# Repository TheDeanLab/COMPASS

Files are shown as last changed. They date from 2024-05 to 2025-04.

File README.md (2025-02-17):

<h1 align="center">
COMPASS

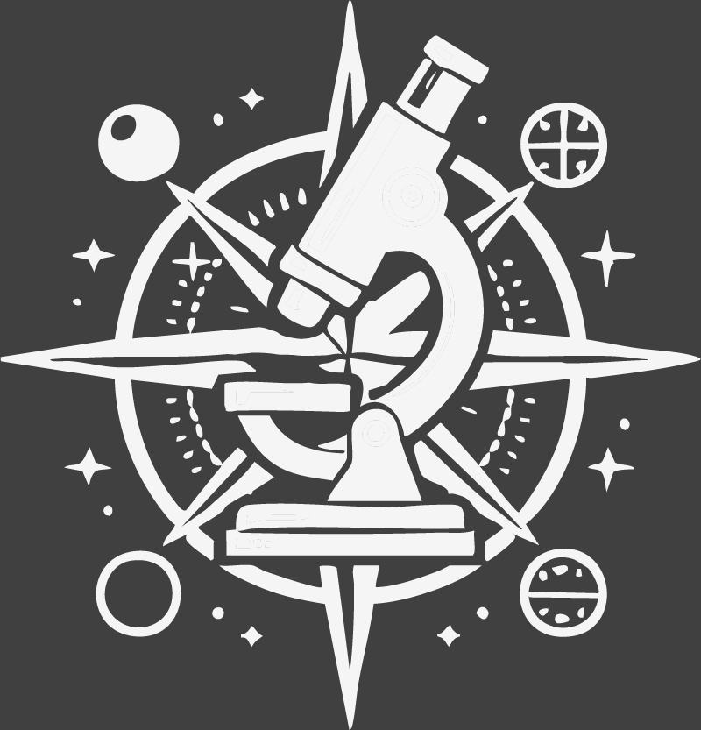
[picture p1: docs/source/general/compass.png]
COMPASS


<h3 align="center">
	Cost-Effective, Open-Source, Light-Sheet Microscopy Solutions for for Sub-Cellular Imaging.
</h3>
</h1>

**COMPASS** aims to democratize high-resolution light-sheet fluorescence microscopy. By combining **modular optomechanics**, **cutting-edge lens simulations**, and **intelligent software**, **COMPASS** enables the rapid assembly of light-sheet fluorescence microscopes that deliver ~235 nm lateral and ~465 nm axial resolution in a user-friendly package.

## Motivation

Cellular behavior is orchestrated by diverse signaling mechanisms that often hinge on **molecular events precisely organized in space and time**. These events include rapid, localized protein interactions that drive processes such as cell division, migration, and differentiation. **COMPASS** addresses the need for **high-resolution live-cell imaging**, empowering researchers to:

- Visualize spatially regulated processes.
- Collect quantitative 3D time-lapse data.
- Bridge molecular probe design and advanced computational image analysis.

## Goal

The overarching goal is to provide a **modular, cost-effective 3D light-sheet microscope** that:
- Can be assembled with minimal prior optics expertise.
- Consistently achieves ~235 nm lateral and ~465 nm axial resolution.
- Seamlessly integrates with our user-friendly, **intelligent imaging software** [navigate](https://github.com/TheDeanLab/navigate).
- Streamlines data acquisition, drastically reducing barriers to cutting-edge microscopy.

## Key Features

1. **High-Resolution Optics**  
   - Optical designs extensively **simulated in Ansys Zemax OpticStudio** to ensure robust performance across the visible spectrum.
   - Thorough **tolerance analysis** to maintain alignment and resolution in non-specialist environments.

2. **Rugged Mechanical Design**  
   - **Computer aided design (CAD) with Autodesk Inventor** for stress testing and mechanical reliability.
   - **Xometry** manufacturing ensures precision component fabrication.
   - **Dowel pins** and **Thorlabs Polaris mounts** allow reproducible alignment of optical elements.

3. **Easy-to-Source Components**  
   - Optics primarily sourced from **Thorlabs**, with **Polaris mounts** for stable positioning.
   - Motion control solutions (X, Y, Z, Focus, Sample Scanning) from **Applied Scientific Instrumentation**.
   - Open-hardware ethos with minimal custom parts to reduce cost and wait times.
   - Detailed step-by-step assembly instructions,

4. **Intuitive Control Software**  
   - Built to interface seamlessly with [navigate](https://github.com/TheDeanLab/navigate).
   - Automated routines for calibration, 3D volume acquisition, and intelligent imaging.

## Getting Started

- **Review the [Documentation](https://thedeanlab.github.io/COMPASS/)**
- **Procure Hardware**
- **Download and Install** [navigate](https://github.com/TheDeanLab/navigate)
- **Assemble Hardware**
- **Optimize Alignment**
- **Validate Performance**

## Authors

- John Haug, Ph.D.
- Kevin M. Dean, Ph.D.

## Funding

- **UTSW-UNC Center for Cell Signaling Analysis**  NIH NIGMS RM1GM145399
- **Center for Metastatic Tumor Imaging**  NIH NCI U54CA268072

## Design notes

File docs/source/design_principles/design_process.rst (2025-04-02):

.. _design-home:

##############
Design Process
##############

---------------

Initial Lens Selection
______________________

Prior to starting optical simulations in Zemax, it's convenient to start with straightforward
calculations to determine which lenses to use in the optical train to achieve the desired field of view (FoV) for your
detection path. In our case, our detection path consisted of a 400 mm tube lens and a Nikon 25x/1.1 numerical aperture (NA) immersion detection objective.

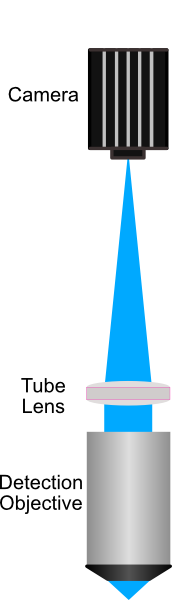
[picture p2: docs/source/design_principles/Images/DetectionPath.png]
Schematic of a standard, widefield detection path.


   **Figure 1:** A simple schematic for a widefield detection path. Here, a detection objective captures light, which is then focused onto the active sensor of a CMOS camera using a tube lens.

.. sidebar:: **Calculating the Focal Length of an Objective**
   :class: sidebar-note

   The focal length (:math:`f`) of a microscope objective can be determined using the **nominal focal length** of
   the manufacturer's standard tube lens and the **objective’s magnification**:

   .. math::

      f = \frac{f_{\text{tube lens}}}{M}

   where:

   - :math:`f_{\text{tube lens}}` is the standard focal length of the tube lens.
   - :math:`M` is the nominal magnification of the objective.

   Standard tube lens focal lengths vary by manufacturer:

   - **Nikon / Zeiss**: 200 mm
   - **Olympus**: 180 mm

   **Example Calculation**
   For a **Nikon 25× NA 1.1 objective**, the focal length is calculated as:

   .. math::

      f = \frac{200 \text{ mm}}{25} = 8 \text{ mm}

To determine the target FoV, start with determining the final magnification (M) of the system using the ratio of the focal lengths of the tube lens (*f*:subscript:`TL`) and the detection objective (*f*:subscript:`DO`, Equation 1.).

.. math::

   M = \frac{f_{\text{TL}}}{f_{\text{DO}}}

From there, determine the resulting FoV of the detection path by dividing the total camera sensor size (in mm) by the magnification, and then converting into microns (Equation 2).

.. math::

   \text{FoV} \ (\mu m) = \left( \frac{W_{\text{Sensor}}}{M} \right) \times 1000

For our system, where *f*:subscript:`TL` = 400 mm, *f*:subscript:`DO` = 8 mm, and W :subscript:`Sensor` = 13 mm,
this resulted in a FoV of ~266 :math:`\mu m`, meaning that we want to select lenses in our illumination path
to produce a light sheet as close to 266 :math:`\mu m` in length as we can achieve.

The overarching goal of a standard optical system is to both mold light into a particular shape and direct it to a
particular location. In our case, our optical system works to convert an input gaussian beam into a thin light sheet that illuminates our sample. There are a few sets of criteria that help guide our potential lens selection:

    * As mentioned, we want our final light sheet size to ideally cover the full FoV of our detection path (~266 μm)
    * At the focus of our cylindrical lens, we want the beam spot size to stay under the size of our resonant galvo (12 mm diameter)
    * We need the focal distance between the cylindrical lens and the galvo mirror system to be greater than ~55 mm due to mechanical considerations of the mirror mount used

With these criteria in mind, we can calculate a theoretical estimate of what our beam size is after each of our lenses. We
do this by considering every pair of lenses (i.e. Lens 1 & 2, Lens 2 & 3, ...) as a sort of 4F magnification system,
where the resulting image size of the pairs is determined by the ratio of their focal lengths (*f*:subscript:`n`) as follows:

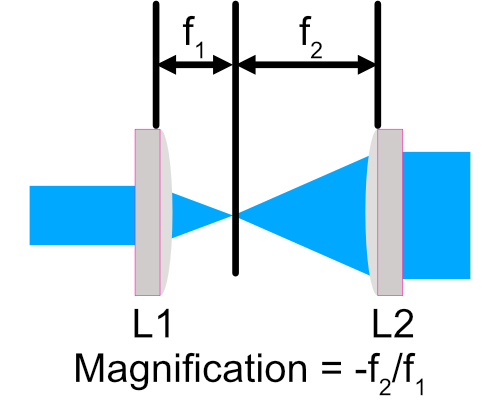
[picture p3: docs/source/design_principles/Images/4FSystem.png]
A diagram of a 4f optical system.


   **Figure 2:** A diagram of a 4f optical system. Here, the ratio of the focal lengths of the lenses determines the magnification of the system.

Essentially, we can cascade these calculations through our lenses and make sure that our choices in their focal
lengths produce our desired beam characteristics as light propagates through the system. In our case,
our chosen system featured 4 lenses from Thorlabs:
`L1 = 30 mm <https://www.thorlabs.com/thorproduct.cfm?partnumber=AC254-030-A>`_,
`L2 = 80 mm <https://www.thorlabs.com/thorproduct.cfm?partnumber=AC254-080-A>`_,
`L3 (Cylindrical) = 75 mm <https://www.thorlabs.com/thorproduct.cfm?partnumber=ACY254-075-A>`_, and
`L4 = 250 mm <https://www.thorlabs.com/thorproduct.cfm?partnumber=AC254-250-A>`_.

We can then take these lens choices and load them into Zemax OpticStudio to verify the characteristics of our system.

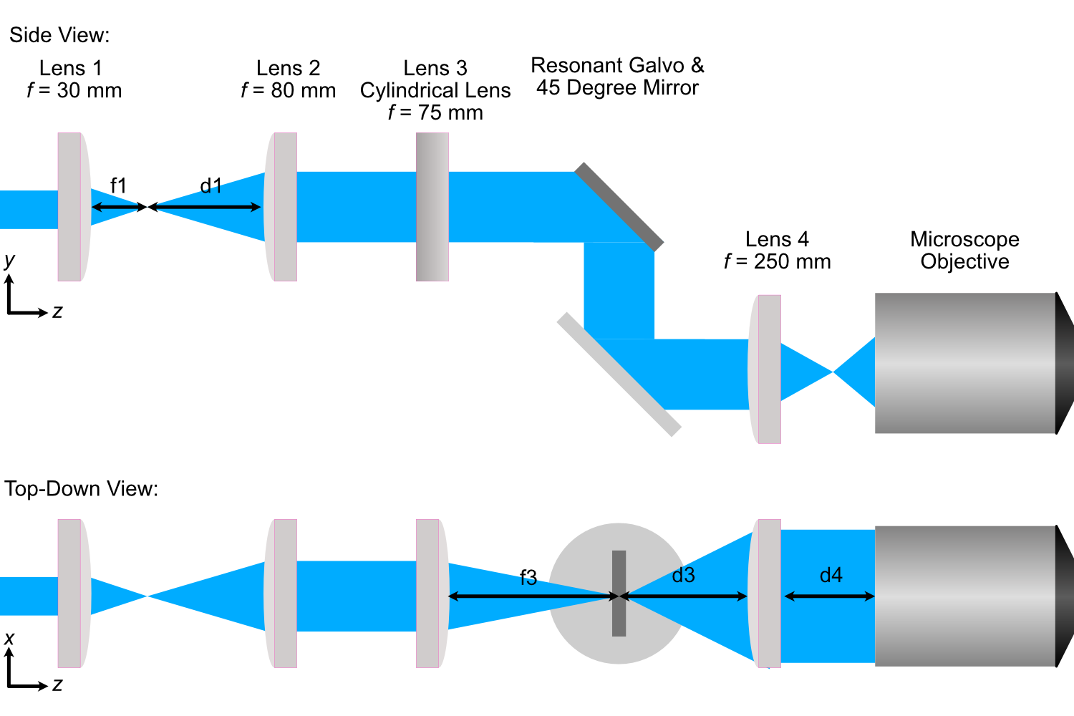
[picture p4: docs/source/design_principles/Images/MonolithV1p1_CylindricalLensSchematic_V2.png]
Top and bottom views of an optical path.


    **Figure 3:** A schematic of the optical path for a light-sheet microscope. The system consists of four lenses, a cylindrical lens, a resonant galvo, a 45-degree mirror, and an illumination objective. Top and bottom views are shown.

----------------

Zemax Simulation Setup Process
______________________________

With our chosen lenses in mind, we can download Zemax files associated with each lens directly from Thorlabs website
and set up our simulation.

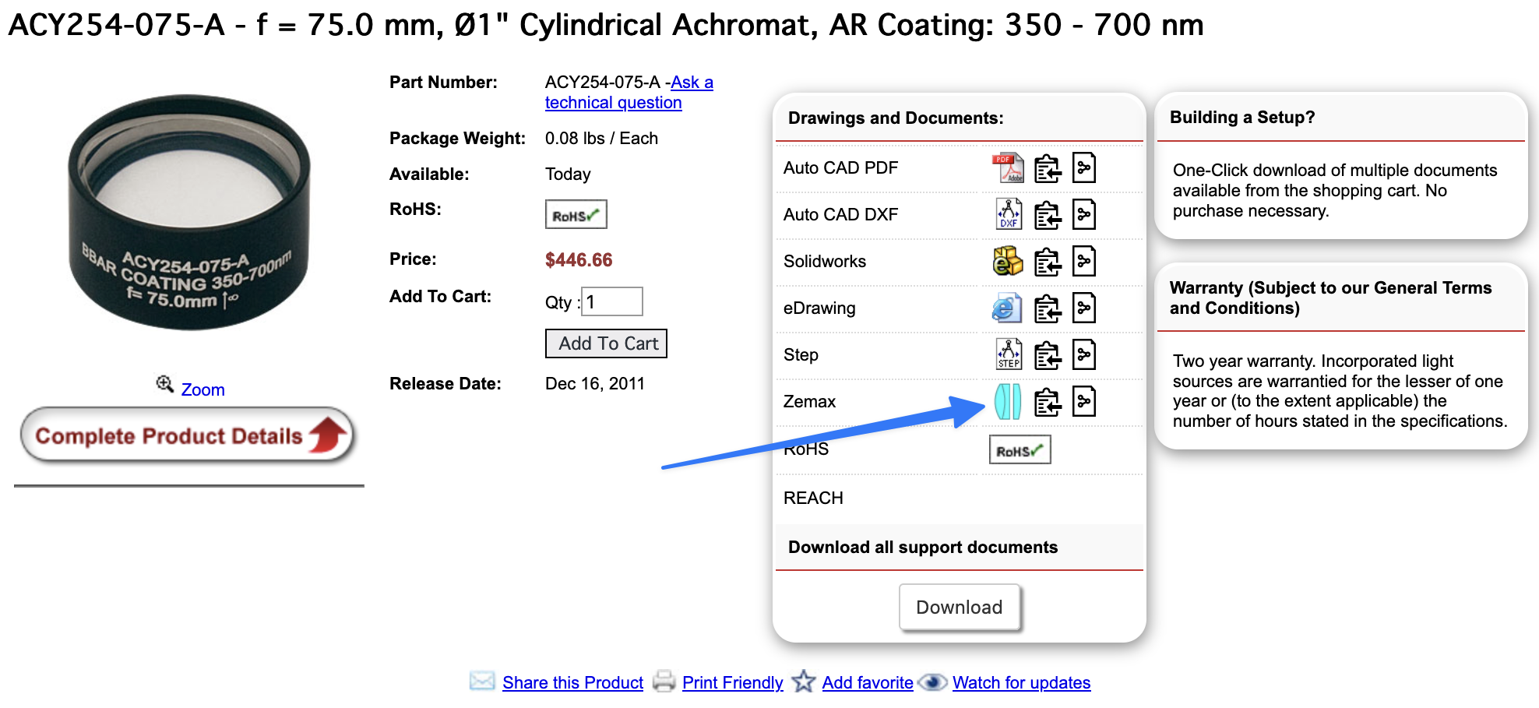
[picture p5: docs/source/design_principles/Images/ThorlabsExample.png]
Thorlabs Zemax Download


    **Figure 4:** An example of a Zemax file download from Thorlabs. The file contains the optical properties of the lens, which can be imported into Zemax OpticStudio.

Here, we use Zemax as a tool to find the optimal placement of all the lenses of our system based on whether or not the input beam should be focusing or collimated after each lens. As a general rule of thumb, one should build optical systems in Zemax in an element-by-element manner instead of adding all the optical elements and trying to then optimize aspects of it. Our general flow involves adding a lens to the system and then optimizing for either either a focused or collimated beam, and then adding in the next lens and doing the same process until all lenses are placed in the system. This is described in more detail below.

For our particular system, our generalized process went as follows:

    1. Create a new file that will be used as our lens assembly file
    2. Set aperture size in Zemax to match our original laser spot size (2.4 mm).
    3. Open the Zemax file associated with Lens 1, then copy and paste the surfaces into our assembly file.
    4. Use the optimization wizard to set a focusing optimization with the distance after L1 (f1) as the variable to find
       the correct position of L1's focus.

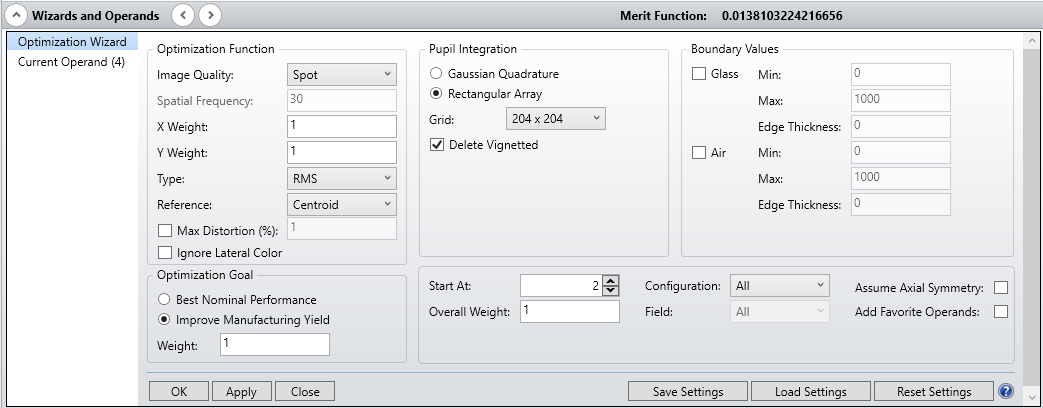
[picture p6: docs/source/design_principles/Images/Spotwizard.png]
Optimization Wizard for Spot Size
    

    **Figure 5:** The optimization wizard in Zemax. Here, the user can set the optimization type and the variable to optimize. In this case, the user is optimizing for spot size.

    5. Run the optimization, then remove the variable for f1.
    6. Open the Zemax file associated with Lens 2, then copy and paste the surfaces into our assembly after Lens 1
    7. Use the Optimization Wizard to set an angular (collimation) optimization, with the distance between L1's focus and L2 (d1) as the variable.

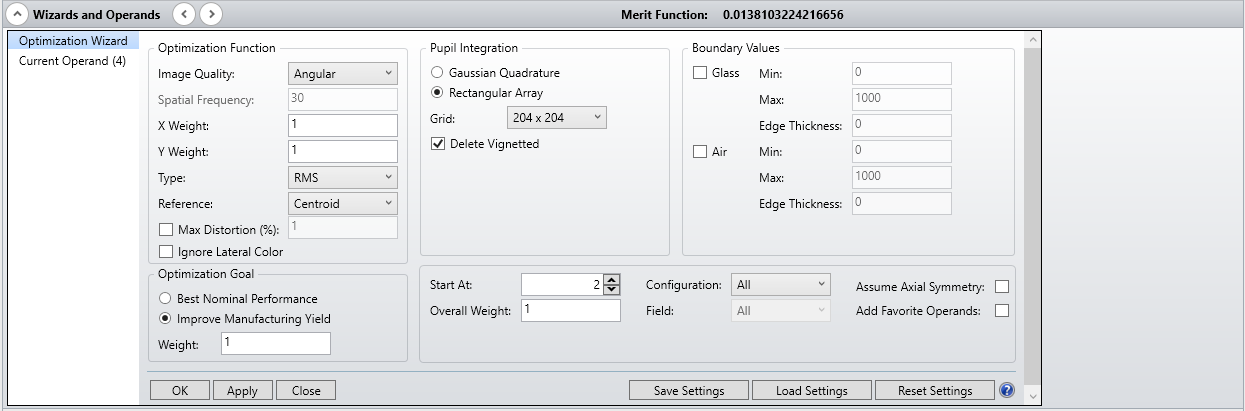
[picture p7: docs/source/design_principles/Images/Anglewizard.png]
Optimization Wizard for Collimation
    

    **Figure 6:** The optimization wizard in Zemax. Here, the user can set the optimization type and the variable to optimize. In this case, the user is optimizing for collimation.

    8. Optimize, then remove the variable for d1.
    9. Open the Zemax file associated with Lens 3, then copy and paste the surfaces into our assembly after Lens 2.
    10. Use the optimization wizard to set an *X*-focusing optimization with the distance after L3 (f3) as the  variable.
    11. Optimize, then remove the variable for f3.
    12. Place in resonant galvo and 45 degree mirror surfaces at the location of f3.
    13. Open the Zemax file associated with Lens 4, then copy and paste the surfaces into our assembly after the 45 degree mirror.
    14. Use the optimization wizard to set an *X*-collimation optimization with the distance between the 45 degree mirror and L4 (d3) as the variable.
    15. Optimize, then remove the variable for d3.
    16. Open the Zemax file associated with our Illumination Objective, then copy and paste the surfaces into our assembly  after L4.
    17. Use the Optimization Wizard to set an *X*-focusing Optimization with the distance between L4 and the objective (d4) as the variable.
    18. Optimize

----------------

Zemax Simulation Analysis
_________________________

Within Zemax, there are numerous analysis tools available to investigate different characteristics of optical systems. Our analysis will primarily be guided by the Geometric Image Analysis, Huygen's PSF, and Through Focus Spot tools. Zemax innately uses geometric ray tracing in most all of its operations like beam optimization. This is generally-acceptable for most optical systems; however, as our output light sheet size approaches the diffraction limit ( :math:`\frac{\lambda}{2NA}` ), we need to make sure to also consider the effects of diffraction in our analysis.

The Huygen's PSF analysis tool is how we incorporate effects of diffraction into our analysis; where we anticipate results from this analysis to be more in-line with what would be seen on the physical system. Based on the cross section of our Huygen's PSF analysis, we can see that our expected Full-Width Half-Max (FWHM) of the light sheet is expected to lie somewhere around 0.376 :math:`\mu m`.

We compare the results of these two analyses for our optimized illumination path below, where we show the full XY profile
as well as cross-sections through the center row of both beam profiles. In this case, the FWHM of both analyses ends up
being quite similar at ~0.37 :math:`\mu m`.

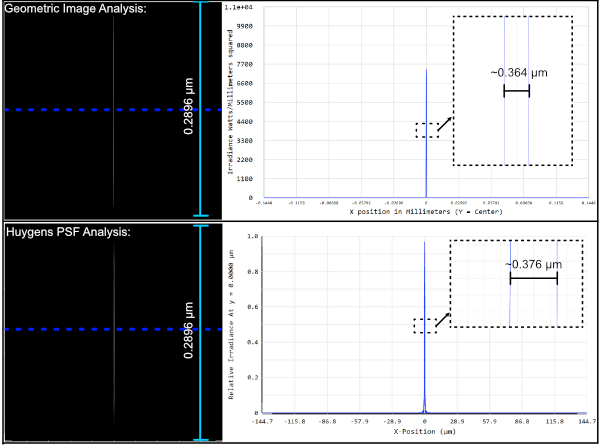
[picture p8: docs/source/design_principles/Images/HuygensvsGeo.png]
Comparison of Geometric Image Analysis and Huygen's PSF analysis for our optimized system


    **Figure 7:** A comparison of the Geometric Image Analysis and Huygen's PSF analysis for our optimized system. The FWHM of the light sheet is expected to be around 0.376 :math:`\mu m`.

Through Focus Spot analysis allows us to essentially see the evolution of the light sheet through the point of focus, where we can then estimate a sort of range where we expect the width of the light sheet to be thin enough for our imaging purposes, where the maximum usable light sheet width is the FWHM at the focus multiplied by :math:`\sqrt{2}`. The optimized illumination path simulation files are available in the `Zemax <https://github.com/TheDeanLab/altair/tree/main/downloads/base/zemax>`_ folder of our repository.

----------------

Zemax Tolerance Analysis
________________________

When considering building physical systems using Zemax, an additional analysis tool known as tolerancing becomes increasingly important. No physical system is perfect, and tolerancing is essentially the process of understanding how sensitive different elements in a system are to various perturbations. This can be along the lines of how sensitive the collimation or magnification of a 4F system is to small physical displacements of the two lenses that comprise it. Similarly to Zemax's optimization process, tolerancing also utilizes a merit function. This merit function is fully customizable, and serves to define how well a particular system is performing. In the case of our system, we chose our merit function to factor in both the size and displacement of the output light sheet relative to the perfectly optimized instance. Our merit function used in Zemax is also shown below, where there are 4 operands that track the size and position of the beam in both x and y.

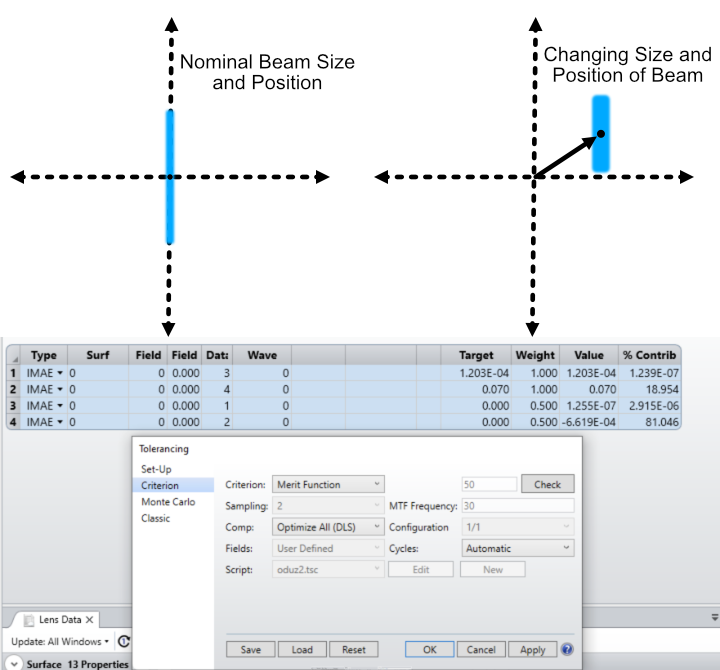
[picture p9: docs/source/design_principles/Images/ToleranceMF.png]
Tolerance Merit Function


    **Figure 8:** The merit function used in our Zemax tolerancing analysis. The merit function is used to evaluate the performance of the system based on the size and position of the output light sheet.

With a merit function criteria set, the next step is to designate which elements of the system will change and by how much. In our case, we wanted to associate our tolerance analysis with the machining tolerances given by fabrication companies. In general, looking across different companies, the standard machining tolerance is around +-0.005" and the finer machining tolerance is around +-0.002". For our analysis, we wanted to understand how angular deviations in elements due to machining tolerances in the alignment dowel pins would affect overall system performance. This is depicted below, where in the worst case scenario of one pin being offset +0.005" and the other -0.005" the resulting angular offset would be around 1.45 degrees.

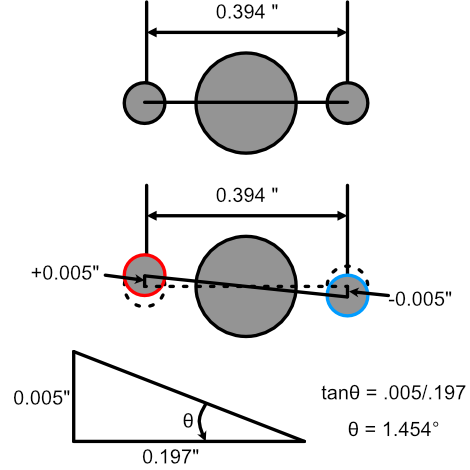
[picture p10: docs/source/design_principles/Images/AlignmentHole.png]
Angular offset of elements imparted by machining tolerances of dowel pin holes


    **Figure 9:** The angular offset of elements due to machining tolerances of alignment dowel pin holes. In the worst case scenario, the angular offset is around 1.45 degrees.

In addition to perturbations to a system, in tolerancing analysis a compensator can also be defined as a sort of designated element that can be changed in ways to try to mitigate effects of other elements in the system being tweaked. In our case, we define the xy position of our illumination objective as a compensator with a range of +-0.25mm, which matches the xy translation adjustment associated with our `objective mount used <https://www.thorlabs.com/thorproduct.cfm?partnumber=POLARIS-1XY>`_.

The basic way in which this analysis works is that Zemax performs a designated number of Monte Carlo simulations, each with a different perturbation made to the system, and evaluates the merit function for each of those systems. Based on the change to the merit function for each of these instances, tolerancing outputs a report that describes the sensitivity of the merit function to each of the different elements in the system. In some cases, tolerancing analysis gives information as to how much . An example of this is for a lens designer tolerancing the radii or material properties of a lens to ensure it's focal length stays above or below a certain value. For our system though, even with our designated merit function, it is difficult to directly ascribe a sort of cutoff value of the merit function as acceptable, and so we primarily use tolerancing analysis as a way to guide us as to general trends of sensitivity in the elements of our system.

This is shown below, where in this instance we can see that in the case of our system, the element corresponding to the 24th surface (the galvo mirror) causes the most change to the merit function as it becomes perturbed. In all cases, the largest perturbations in the system (i.e. when the angular offset of an element is maximum at +-1.45 degrees) results in the largest changes to the merit function.

We also set our tolerance analysis to output the best and worst instances from the Monte Carlo simulations as individual files, and the corresponding geometric image analysis windows are shown for each as well as the nominal optimized case for comparison. It's clear that in the worst case scenario, it looks like the resulting light sheet is shorter in span than that of the nominal and best cases.

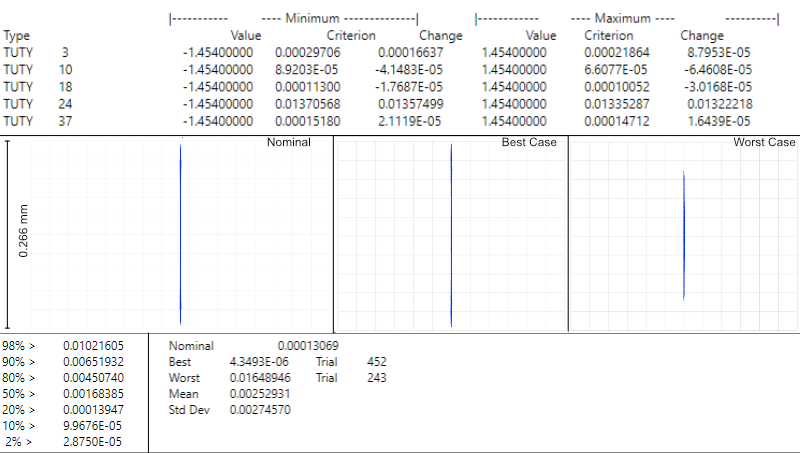
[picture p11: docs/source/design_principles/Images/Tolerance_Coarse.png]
Results of tolerancing analysis when the offset corresponded to +-0.005"


    **Figure 10:** Results of the tolerancing analysis when the offset corresponded to +-0.005". The merit function is used to evaluate the performance of the system based on the size and position of the output light sheet.

To understand how tighter tolerances might affect system performance, we set our angular offset to correspond to tighter machining tolerances offered online at +-0.002". Typically, tighter machining tolerances correspond to an increase in price, so understanding if higher tolerances would benefit a system is beneficial. We can the same tolerance analysis as before, but this time with an angular offset of +-0.581 degrees, and show the results below. In this analysis, once again the element that affects the system most adversely is the galvo mirror element. The deviations in the resulting merit functions from this element are about a tenth of that of the larger machining tolerance case. Visually, in the worst case example, one can see that the resulting light sheet looks much closer to the nominal case than before as well.

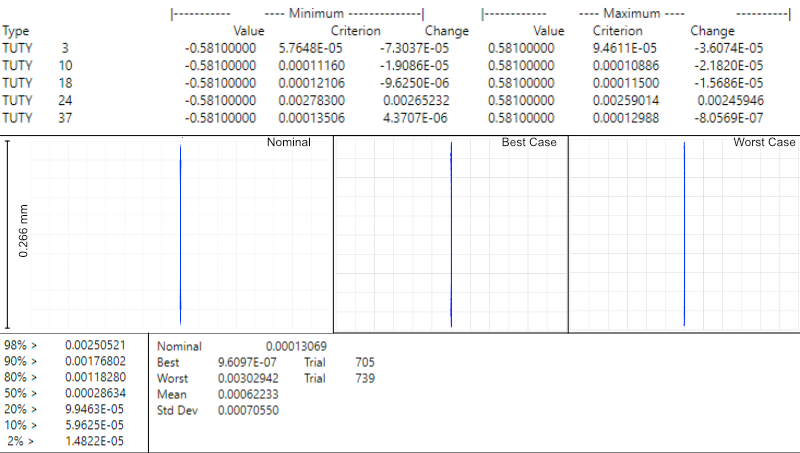
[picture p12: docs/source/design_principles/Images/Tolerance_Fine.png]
Results of tolerancing analysis when the offset corresponded to +-0.002"


    **Figure 11:** Results of the tolerancing analysis when the offset corresponded to +-0.002". The merit function is used to evaluate the performance of the system based on the size and position of the output light sheet.

The results of our tolerancing analysis, as well as the associated lens files for our best and wort case instances for both fine and coarse tolerancing are available `here <https://github
.com/TheDeanLab/altair/tree/main/downloads/base/zemax>`_.

----------------

Baseplate Design
________________

When satisfied with the results of simulations, the optimized values in Zemax can then be used to design
our baseplate. This process involves taking the optimized distances between our various optical elements
and then considering how each of those elements are mounted in a physical system, as in Zemax all of the elements are effectively suspended in midair like below:

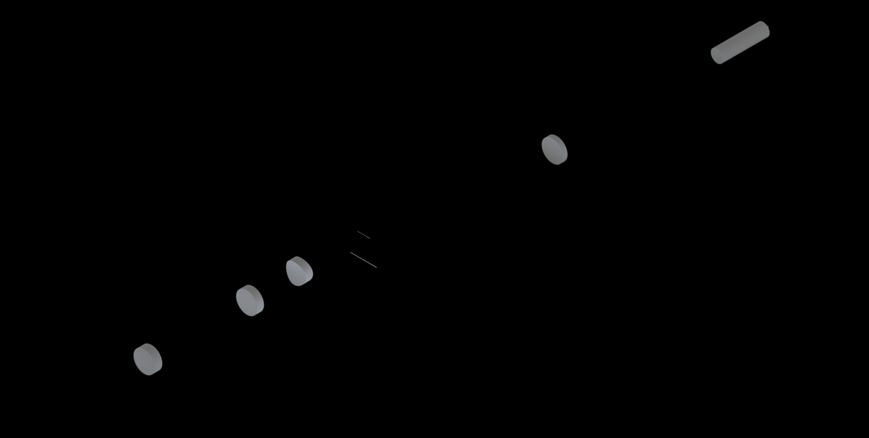
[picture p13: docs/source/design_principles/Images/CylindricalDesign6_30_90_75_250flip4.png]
Zemax Elements Floating


    **Figure 12:** A Zemax diagram of the elements in our system. Here, the elements are shown floating in midair.

For mounting our elements, we utilize the `Polaris <https://www.thorlabs.com/navigation.cfm?guide_id=2368>`_ line from Thorlabs, which are designed with long-term stability and alignment in mind. Each component is characterized in part by two dowel pin alignment holes to ensure subsequent mounted elements are aligned along a specific axis. In the baseplate design, we are essentially deciding on the location for the mounting holes of the Polaris posts we're using, which is not the same as the locations of the elements themselves from Zemax.

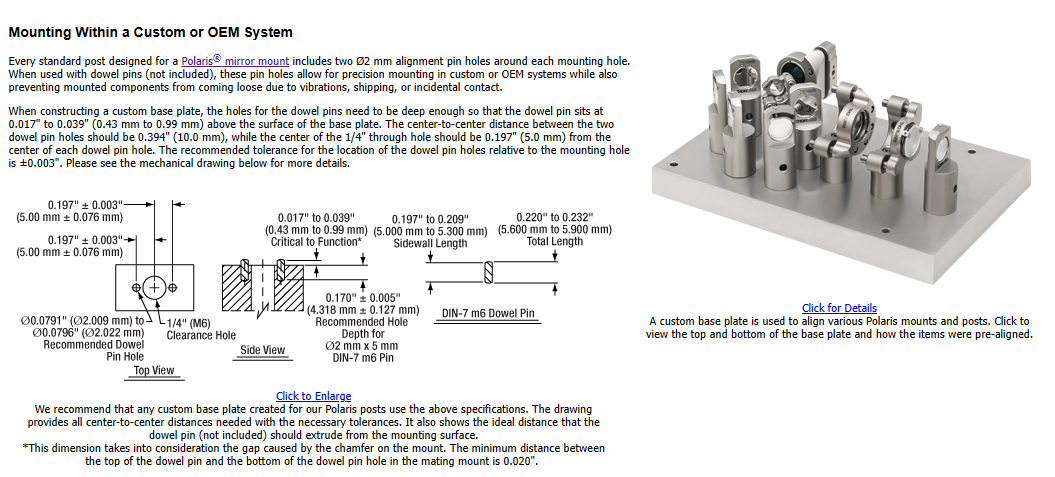
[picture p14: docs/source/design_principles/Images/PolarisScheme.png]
Polaris Scheme


    **Figure 13:** A schematic of the Polaris mounting system. The system is characterized by two dowel pin alignment holes to ensure subsequent mounted elements are aligned along a specific axis.

While we are able to use most of our element mounts from the Polaris line, for the cylindrical lens L3 we needed a mount capable of rotating the lens, which at this time is not something available from Thorlabs. In our case we designed an additional mounting element that allows the use of a basic Thorlabs
`RSP1 rotation mount <https://www.thorlabs.com/thorproduct.cfm?partnumber=RSP1>`_, but still ensures alignment with the other Polaris elements. The CAD file for this mount is available for download `in our CAD directory <https://github
.com/TheDeanLab/altair/tree/main/downloads/base/cad>`_.

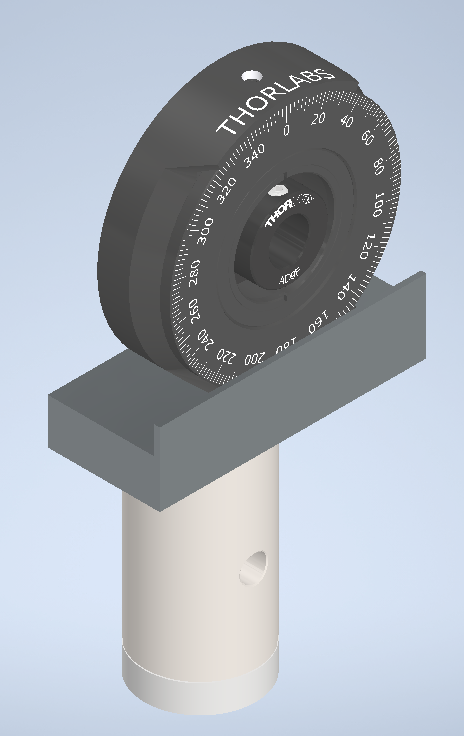
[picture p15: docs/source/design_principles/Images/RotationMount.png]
Rotation Mount Adapter


    **Figure 14:** A schematic of the rotation mount adapter. The adapter allows for the rotation of the cylindrical lens while ensuring alignment with the other Polaris elements.

With the method in which each of the elements needs to be mounted decided upon, we then went over the product schematics for each mount to understand the z-displacement that they impart upon the element mounted within them relative to where the Polaris post central mounting hole would need to be. This idea is depicted below, where when considering how to space two lenses from each other there is essentially three components to take into account:

    1. The distance between the lenses decided from simulation
    2. The thickness of the lenses themselves
    3. The distance between the center of the Polaris post and the start of the lens in the mount

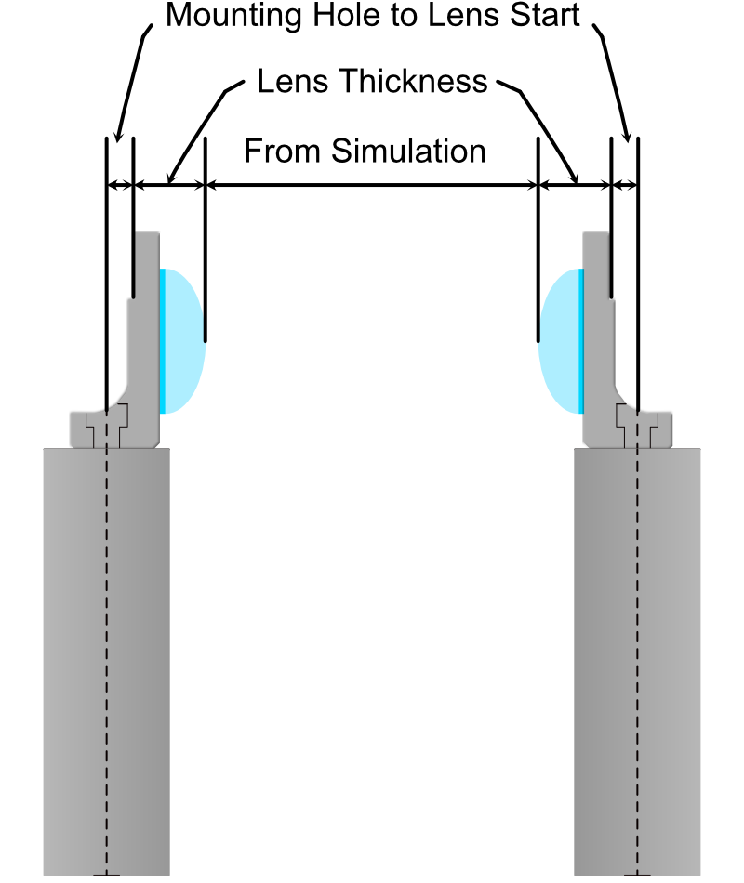
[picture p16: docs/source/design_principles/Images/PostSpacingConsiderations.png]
Post Spacing Considerations


    **Figure 15:** A schematic of the considerations for spacing two lenses from each other. The distance between the lenses is decided from simulation, the thickness of the lenses themselves, and the distance between the center of the Polaris post and the start of the lens in the mount.

Once the locations of the mounting holes were determined, we used Autodesk Inventor to design the full baseplate. The baseplate is essentially just a mounting hole and the two dowel pin holes for every element, as well as four mounting holes for the baseplate itself. These four baseplate mounting holes were spaced in increments of inches such that the baseplate can either be screwed directly into an optical breadboard table or into additional posts that can keep the assembly at a desired height.

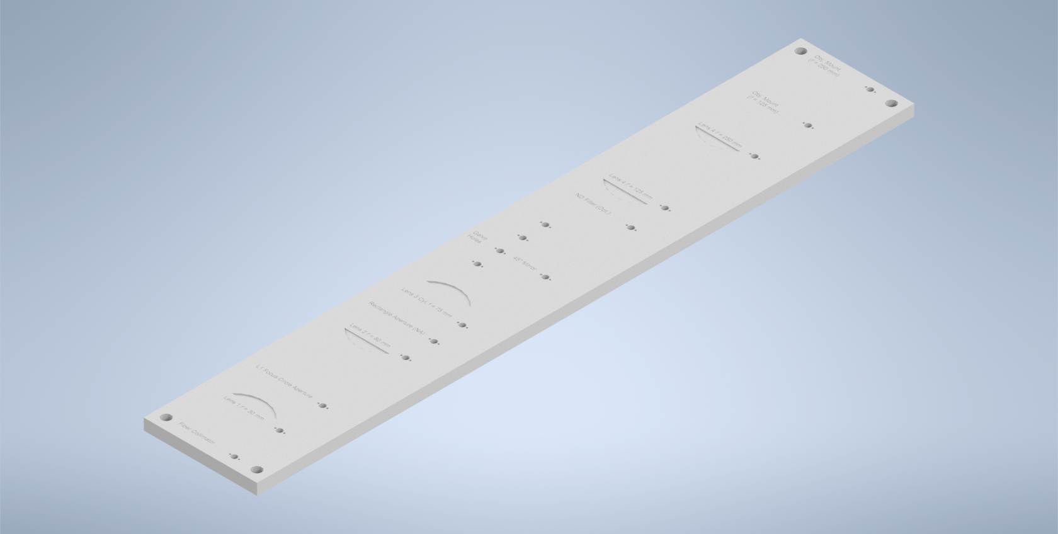
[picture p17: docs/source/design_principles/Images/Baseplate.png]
Baseplate


    **Figure 16:** A schematic of the baseplate. The baseplate is characterized by mounting holes for each element and four mounting holes for the baseplate itself.

With the baseplate designed, our final assembly for our illumination path looks as follows:

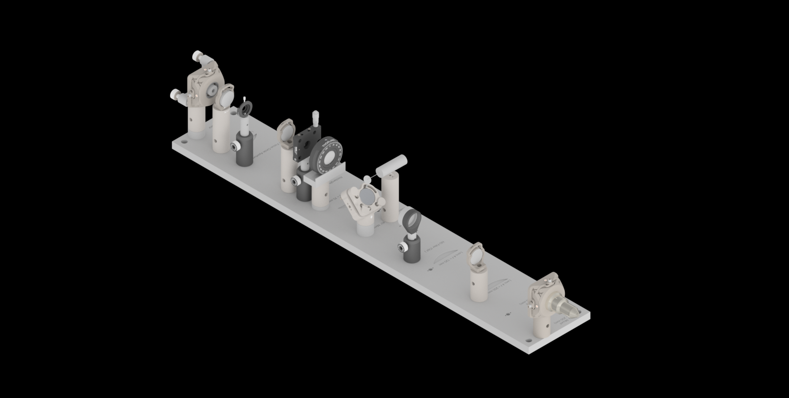
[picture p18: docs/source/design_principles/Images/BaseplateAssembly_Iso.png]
Baseplate Assembly Iso


    **Figure 17:** An isometric view of the baseplate assembly.

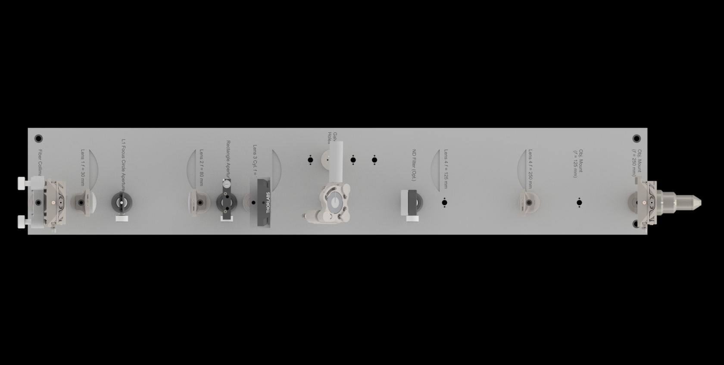
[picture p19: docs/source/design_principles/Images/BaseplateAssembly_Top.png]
Baseplate Assembly Top


    **Figure 18:** A top view of the baseplate assembly.

The CAD files for our baseplate design are available in the following `GitHub repository <https://github
.com/TheDeanLab/altair/tree/main/downloads/base/cad>`_.

----------------

Physical Coordinate Definitions
_______________________________

It should be noted briefly that when discussing our physical microscope systems using navigate software, the definitions for the coordinate axes is different than that of our simulations. This is due to a difference in standardized definitions for the axes in our previous systems and how Zemax defines these same axes. This difference is depicted in the picture below:

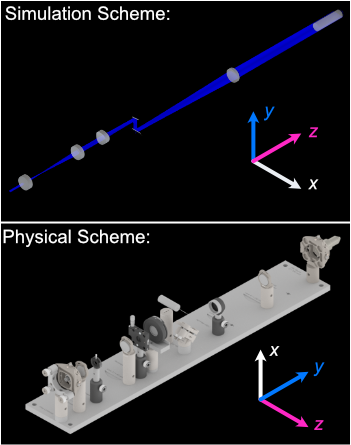
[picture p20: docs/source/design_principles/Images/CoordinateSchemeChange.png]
Difference in coordinate axes for simulation and physical setup


    **Figure 19:** A schematic of the difference in coordinate axes for simulation and physical setup.

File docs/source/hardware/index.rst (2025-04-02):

.. _hardware-home:

################################
Room and Hardware Considerations
################################

Installing a **Altair** system requires careful planning to ensure optimal performance and long-term stability.
Proper preparation includes considerations for **room setup, optical table selection, acquisition computer
specifications, laser identification, and environmental controls**. Each of these factors plays a significant role
in instrument performance. Consequently, before beginning the installation process, we recommend evaluating the
information, some of which is provided simply as educational resources.

.. toctree::
   :caption: Preparing for Altair
   :maxdepth: 2

   room_preparation.rst
   table.rst
   computer.rst
   lasers.rst

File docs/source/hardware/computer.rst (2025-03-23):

.. _computer-home:

###############################
Computer Specifications
###############################

Modern scientific cameras are capable of capturing images at very high frame rates.
For example, the Orca-Lightning from Hamamatsu, when imaging a region of interest of
4608x128, can image at 2203 frames per second, totalling 1.3 terapixel per second. It
is important to have a computer that can handle this data rate. For many applications, we recommend Colfax International's SXP9000 workstation, which
includes several convenient features, including:

-   A large number of high-speed peripheral slots. While originally designed to host
    GPU cards, these slots can be used for other high-speed peripherals, such as frame
    grabbers.
-   A high-speed NVMe SSD, which can achieve upwards of 20 GB/s under ideal
    conditions.
-   10GbE LAN - 10G Ethernet or faster, if supported by your institution, is highly
    recommended for transferring data to and from the computer. This computer provides
    this high-speed connection without necessitating an additional network card, freeing
    up precious space in the computer.
-   USB-C ports that can be used for image display, keyboard, and mouse. Again, by
    eliminating the need for a graphics card, available space is available to other
    peripheral devices.
-   Redundant power supplies - in the event of a power supply failure, the computer will
    continue to operate. Moreover, they will be able to drive some of the more power-hungry
    components, such as frame grabbers.
-   Aggressive cooling - the computer is designed to handle the heat generated by the
    high-speed components.

---------------

Standard Build
______________

A general build for a imaging computer is as follows:

-   Windows 10 Pro. This is the most common operating system for scientific imaging
    applications.
-   2x Intel Xeon Silver CPUs Total of 16 Cores/32 Threads @ 3.2GHz. Higher speeds,
    and a greater number of cores is advantageous but expensive.
-   128 GB of 3200 MHz DDR4 RAM. This is more than sufficient for most applications.
-   800 GB M.2 NVMe SSD. Used to host and run the operating system.
-   20 TB 7200 RPM SATA HDD. Used as a 'cold storage' for long-term data storage.
-   NVIDIA T1000 Video Card. This is a low-end video card that can be used to drive
    displays and perform some basic image processing. The priority for this computer
    is driving the microscope and acquiring data, so a high-end video card is not necessary.
-   Intel X710-T2L 10GbE Card. If the motherboard does not provide 10GbE, this card can
    be used to provide high-speed network connectivity.
-   7.68 TB NVMe SSD. Used as the primary data drive.

.. note::

    Recently, Hamamatsu released a Linux driver for their cameras. Linux
    provides several advantages to Windows-based operating systems, including read
    and write operations with lower overhead. This is especially important for next-generation
    file formats, such as N5, OME-Zarr, and Zarr, all of which break large
    images up into smaller 'chunks' that can be read and written independently. To
    learn more, we recommend reading
    `Moore et al. 2021 <https://pubmed.ncbi.nlm.nih.gov/34845388/>`_, and
    `Moore et al. 2023 <https://pubmed.ncbi.nlm.nih.gov/37428210/>`_.

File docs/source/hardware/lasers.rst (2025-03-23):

.. _lasers-home:

#############
Laser Sources
#############

When designing a microscope for imaging, the choice of light source is critical. In
general, an ideal imaging system will provide fast spectral switching, high light
throughput, provide stable power emission, have a long lifetime, be cost-effective,
and be low complexity.

Several light have been developed for use in microscopy, including arc lamps, light
emitting diodes (LEDs), solid state lasers (including fiber lasers, optically pumped
semiconductor lasers, diode pumped solid state lasers), supercontinuum lasers, and
ultrafast lasers (including ti-sapphire lasers). A few key parameters to consider are
discussed below.

---------------

Linewidth
_________
One key aspect of any light source is the linewidth of its emission. This is the
spectral width of a light source in nanometers of the spectral density of the emitted
electric field. It can also be reported in wavenumbers (cm :sup:`-1`) or frequency (Hz).
Narrow linewidths enable more aggressive detection bands, reduced bleedthrough, and a
reduced background. LEDs typically have a linewidth of 20-50 nm, which is much broader
than the 0.1-1 nm linewidth of a laser. As such, we prefer lasers for our imaging
systems.

---------------

Beam Divergence
_______________
The M :sup:`2` value of a beam is the degree at which it can be focused to a given beam
divergence angle (e.g., numerical aperture). If you have a higher M :sup:`2` value of
~1.6, it will focused to a laser spot that is 1.6x larger than the diffraction limit.
As such, for high-resolution imaging, it is important to have a low M :sup:`2` value.
We prefer lasers with an M :sup:`2` value of <1.2 for our imaging systems. Fiber lasers,
such as those offered by MPB Communications, provide very low M :sup:`2` values.
However, these systems require external mechanisms for controlling the power output,
which is a major disadvantage. For lasers with high M :sup:`2` values, additional
optics may be necessary to clean up the beam profile, such as a spatial filter.

---------------

Modulation
__________
The ability to modulate the power of a light source is important for many imaging
applications. It is not uncommon to use an acousto-optic modulator (AOM),
acousto-optic tunable filter (AOTF), or electro-optic modulator (EOM) to modulate the
power of a laser. AOMs induce sound waves within a crystal to change the refractive
index of the crystal, which alters the angle of the light at a single wavelength.
Likewise, AOTFs use a variable frequency sound wave to operate at multiple
wavelengths. EOMs, such as a Pockels cell, induce a directionally dependent
change in refractive index in a crystal, which can change the polarization of the
light passing through it. These are especially common in ultrafast laser systems.
Both AOMs and EOMs can be used to modulate the power of the laser, with
rise times of ~5-50 ns and Acousto-optic devices offer rise times 0.25 - 1 ns,
respectively. However, especially for continuous wave (CW) lasers, these devices
serve as a source of additional complexity, cost, and potential failure points. For
example, we have noted that AOMs can be sensitive to temperature changes, which can
lead to drift in the power output. As such, we prefer lasers with built-in modulation
capabilities.

---------------

Vibrations
__________
Many lasers require active cooling, and are often placed directly on the optic table,
which can lead to vibrations. These vibrations can be detrimental to imaging quality,
especially when imaging in soft contexts such as expanded tissues. Nonetheless, if
insufficient cooling is provided, fluctuations in laser emission or instability can
occur.

---------------

Power
_____
The power of the laser that is needed depends critically on the light throughout of
the illumination train, as well as the size of the field of view. While some light
sources such as supercontinuum lasers can provide high power (e.g., >3W), their emission
is spread across a large spectral range, reducing their spectral power density at any
given wavelength to a few mW/nm. We typically recommend lasers with a power of 100 mW
or greater for imaging.

---------------

Recommended Light Sources
-------------------------
For all of these reasons, we recommend the use of optically pumped semiconductor
lasers (OPSLs) for imaging. OPSLs are solid state lasers that use a diode to
optically pump a semiconductor gain medium which can be tuned to adjust the emission
wavelength of the laser. Importantly, OPSLs have a narrow line width (<10 pM), low M
:sup:`2` value, can modulate the laser on microsecond timescales, and achieve high
and stable emission powers.

OPSLs are available from several manufacturers and can typically be driven in either
a constant power or constant current mode. We typically use the former, as the laser
uses active feedback to stabilize the emission power. To eliminate challenges
associated with vibrations, we use single mode fiber-coupled OPSLs, which can be
removed from the optical table provide very nice beam quality.

For our imaging systems, we have used the following lasers:

-   Coherent Galaxy laser combiner and OBIS lasers
-   Oxxius LaserBoxx with LuxX lasers.
-   Omicron LightHub Ultra with LuxX and OBIS lasers.

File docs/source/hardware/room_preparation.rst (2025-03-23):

.. _prep-home:

###############################
Preparation of the Imaging Room
###############################

A common question that we get is how to set up the room for imaging. This section will go over the steps that we took to set up the room for imaging. The stated directions assume that the system will be housed in the United States. If you are in a different country, you may need to adjust the electrical configuration accordingly.

---------------

Power Outlets
-------------------
The first thing to consider is the power outlets. For most imaging systems, you will need standard 120V outlets. If you plan on having a Ti-Sapphire laser, then 240V outlets are likely necessary. We typically like to have power strips on the walls, so that you have plenty to choose from.

---------------

Temperature Control
-------------------
Temperature control is important for imaging. We recommend having a temperature sensor in the room for controlling the temperature in that zone. Otherwise, the electronics and people can heat up the room significantly, which can cause drift in the imaging system. HVAC systems can also be a source of dust. Ideally, the ventilation to the room will be HEPA filtered and the air flow will be directed away from the microscope.

---------------

Painting the Walls
-------------------
We typically paint the walls matte black. The matte black walls are helpful for reducing the glare from the monitor and other sources of scattered light from being detected with the camera.

---------------

Network Connections
-------------------
We recommend having a 10G network or faster for transferring data. This will help with the transfer of large image files that are generated during imaging.

---------------

Curtains
--------
If you expect other people to work in the space at the same time, or if you want multiple microscopes, we recommend having blackout curtains to separate the spaces. If the imaging space does not have a fire sprinkler, then the curtain will likely need a gap between the ceiling and the curtain to meet building regulations.

---------------

House Air
---------
You will need house air operating at ~100 PSI to float the table. Having gas cylinders is not an option, as the tank will likely have to be replaced too frequently.

---------------

Floor Flatness
--------------
The floor should be flat. If the floor is not flat, then the table will need special accessories to make it level.

---------------

External Sources of Vibration
-----------------------------
Make sure that the room is not near any external sources of vibration. This can include elevators, HVAC units, or other heavy machinery. Especially when imaging in soft substrates such as expanded tissues, or reconstituted extracellular matrix environments, vibrations can degrade imaging quality. In general, microscopy rooms in basements are preferable, as they are less likely to be affected by external sources of vibration.

---------------

Water Damage
------------
Also consider worst-case scenarios such as a water leak from the room above. If there is a significant risk that the fire sprinkler system could go off, then you may want to consider mechanisms of protecting the electronics and optics from water damage.

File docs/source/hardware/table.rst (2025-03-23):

.. _table-home:

###############################
Optical Table
###############################

The optical table is the most important part of the imaging room. We recommend a large
table, as it is better to have too much table than not enough. Ideally, the room is
large enough that the table is not completely against the wall, so that you have access
to the entire table.

---------------

Table Height
-------------------
Having a table at the right height makes working at the table more comfortable. We
recommend that the table surface be located approximately 38 - 40 inches from the
floor.

---------------

Table Thickness
-------------------
We typically purchase tables with an 18" thickness. In theory, thicker tables better
dampen vibrations arising from on the table itself, including fans from cameras,
voice coils, stages, etc. Practically, in our experience, the table thickness helps
mitigate vibrations arising from the building itself as well. 

---------------

Table Accessories
-------------------
We recommend getting a table with a shelf and power strips. The shelf is useful for
storing electronics and other equipment in a location where their vibrations will not
be coupled to the table.

---------------

Hole Pattern
-------------------
All of our optical mounts are designed to fit the 1” grid pattern with 1/4”-20 holes.
If you would like to have metric holes, you will need to customize the mounts to fit the
table.

---------------

Casters
-------------------
Casters serve as a very convenient mechanism for moving the table around. We thus
highly recommend getting a table with casters. Otherwise, most tables are
sufficiently heavy that they will not be able to be moved once installed.

---------------

Vibration Damping
-------------------
Many vibration damping systems actually amplify vibrations at low frequencies, which
are common building-associated vibrations. To mitigate this, we recommend using a
tuned damping system. TMC provides and UltraDamp series of isolation systems that

---------------

Table Installation
-------------------
We recommend following the manufacturer’s instructions for installing the table.
Importantly the frame, and the table top should be level in order to achieve the best
performance. Given the weight of the table, it is likely that professional
installation will be required.

---------------

Recommended Table
-------------------
We typically purchase Performance Series CleanTop Research Grade 784 Series Optical
Tables from TMC. These tables are available in a variety of sizes, and the weight can
be estimated from the lateral dimensions of the table and its thickness. To increase
the weight and damping capacity of the table, we opt for the 18" standard thickness.
This is placed on a set of 14-Special UltraDamp legs that are equipped with casters
and provide a 20" working height, and a total overall table height of 38".

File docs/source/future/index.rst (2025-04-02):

.. _future-home:

###############
Future Releases
###############

The development of **Altair** is an ongoing effort, with future iterations aimed at increasing both **complexity and capability** to support volumetric imaging across a diverse range of specimens and experimental contexts. Each implementation will be **versioned** and accompanied by comprehensive documentation, ensuring that researchers can **replicate and modify** the system at a fraction of the cost of commercial alternatives. To foster **open development and community-driven innovation**, we encourage users to **request features and provide feedback** publicly via
`Altair GitHub Issues <https://github.com/TheDeanLab/altair/issues>`_.

The projected design roadmap includes:

- **Sample-scanning light-sheet microscope** for imaging cells on glass coverslips.
- **Sample-scanning Axially Swept Light-Sheet Microscope (ASLM).**
- **Laser-scanning Axially Swept Light-Sheet Microscope.**
- **Sample-scanning Oblique Plane Microscope (OPM).**
- **Laser-scanning Oblique Plane Microscope.**

Beyond these core designs, we aim to develop **modular additions** that extend Altair’s functionality, including **optogenetic stimulation** for targeted cellular activation and **multiplexed imaging** for simultaneous readouts of multiple probes. Through this iterative approach, Altair will continue evolving as a **highly adaptable, cost-effective, and open-source platform** for cutting-edge volumetric imaging.

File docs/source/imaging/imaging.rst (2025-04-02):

.. _imaging-home:

###############
Imaging Process
###############

Imaging Configurations
^^^^^^^^^^^^^^^^^^^^^^

Our sample chamber features three ports that provide two distinct imaging configurations shown below: the first is a
traditional light-sheet imaging scheme, where illumination and detection objectives are placed orthogonally to each
other, and the second is one where the illumination and detection objective are placed coaxially with each other. The
first configuration should be thought of as the default imaging setup for the microscope, and the second allows one to
observe and characterize the produced light sheet itself. The port not in use should be sealed, which we do using a
silicon or rubber seal that's able to be fixed onto the exterior of the port using screws. In addition, it should be
noted that our sample chamber design utilizes two sequential layers of O-rings in each of the ports to both secure
the objectives and prevent any leaking.

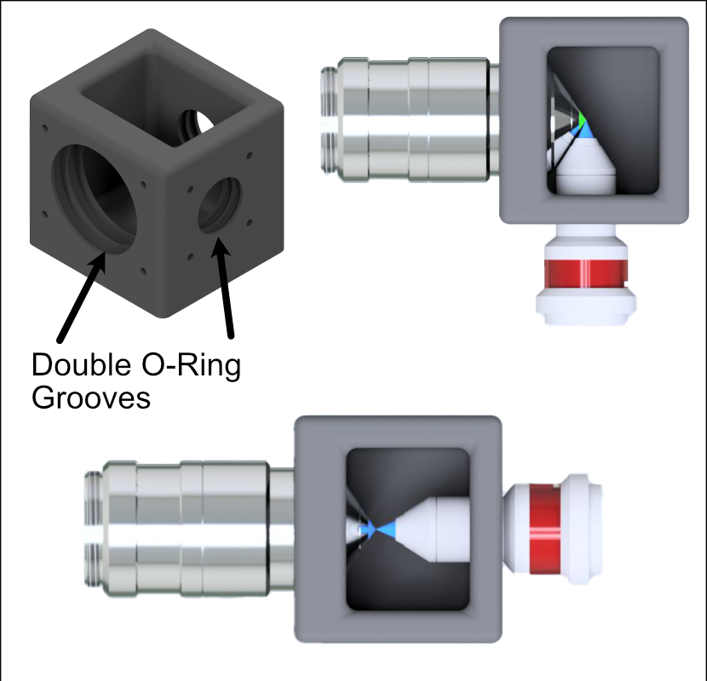
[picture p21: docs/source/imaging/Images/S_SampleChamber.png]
Two imaging configurations for the sample chamber design


    **Figure 1** Two imaging configurations for the sample chamber design

-------------

Visualization of Axes Mapping
^^^^^^^^^^^^^^^^^^^^^^^^^^^^^

In our system we essentially have 5 different translation stages at work: the standard x,y, and z axes, an additional
stage along the z axis to control the focus of the detection path (f), and and axis associated with the piezo positioned
such that its normal is 60.5 degrees away from the y-axis.

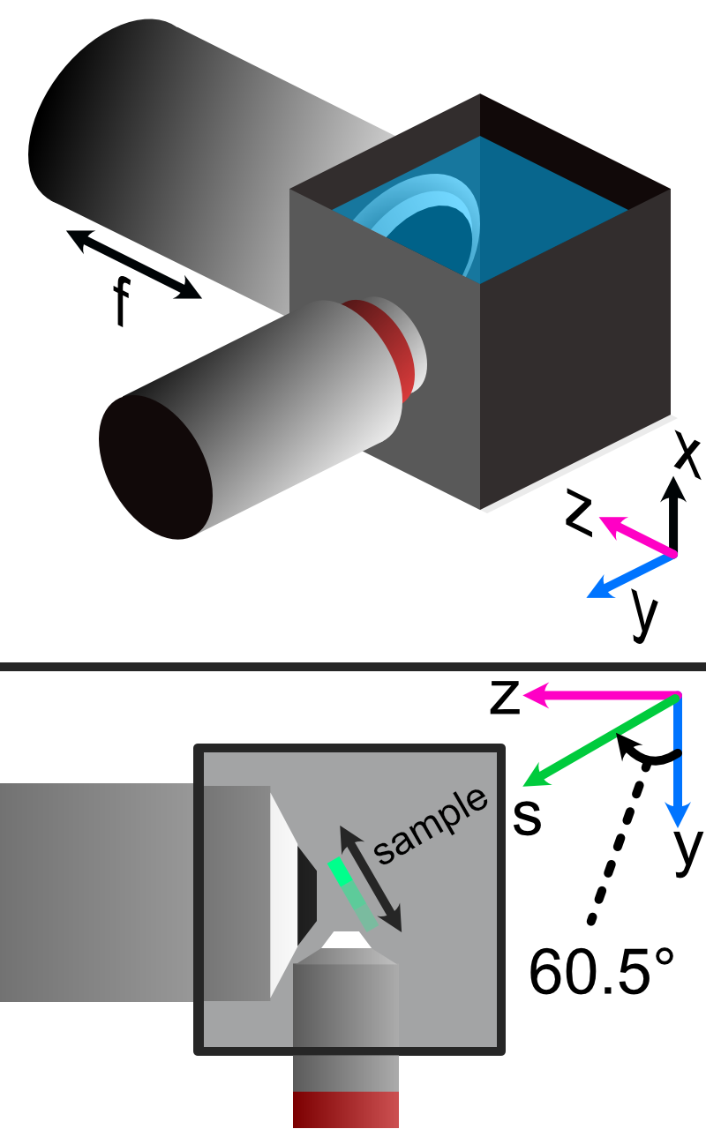
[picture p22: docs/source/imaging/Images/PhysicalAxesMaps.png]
Layout of how the axis of the system are mapped


    **Figure 2** Layout of how the axis of the system are mapped

-------------

Minimizing Spherical Aberrations
^^^^^^^^^^^^^^^^^^^^^^^^^^^^^^^^

Once the system has been assembled to the point of being able to take image stacks, the process of
minimizing the effects of spherical aberrations can begin. Spherical aberrations are typically
introduced into optical systems due to the surface curvature of different lens elements. This
type of aberration typically presents itself visually as a sort of stretching or bending of the focus
of light in the system. Certain microscope objectives, such as the Nikon 25x/1.1 NA that we employ in this setup,
have a built-in collar that can be adjusted to minimize spherical aberration.

In our system, we expect the effects of spherical aberrations to be along the axis of our detection path (defined
as z in our imaging scheme). In order to visualize these effects and adjust the correction collar of our objective
to mitigate them, we employ a process of taking a z-stack of fluorescent beads suspended in agarose
and using ImageJ to quickly process those images.

    1. Take a z-stack within navigate of your sample
    2. Open up the z-stack within ImageJ
    3. Reslice the z-stack (Image -> Stacks -> Reslice)
    4. Do a maximum intensity project of the resliced stack (Image -> Stacks -> Z-Projection)
    5. Take note if spherical aberration is present in the projected image.
    6. If spherical aberration is still present, make slight adjustments to the objective
       correction collar and repeat Steps 1-5. Each time you adjust the correction collar, you will likely need to update the focus of the microscope.

As a note, observing the camera live-feed via navigate's "Continuous Scan" mode while adjusting the correction collar
can help to get in the general vicinity of the correct placement of the correction collar. An example of how change in
the correction collar affect live images are shown below for fluorescent beads. Aiming to get to get the beads near the
expected light sheet position to be as in-focus as possible is a general guide for what direction to move the collar;
however, true correction needs to be done with the z-projection method mentioned above.

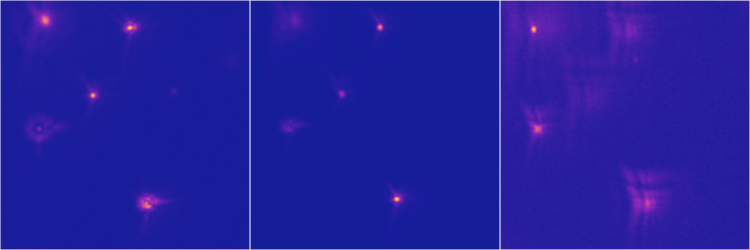
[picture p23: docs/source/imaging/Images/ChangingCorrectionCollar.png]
Correction collar effects


    **Figure 3:** Effects of adjusting the correction collar when imaging fluorescent beads

As a quick example of what an image of a z-projection could look like before and after trying to correct for spherical aberration is shown below. Here, one can see in the top panel that the bead features are essentially smoothed out and fuzzy due to aberrations, while in the bottom panel with adjustments made to the correction collar the beads appear much cleaner and
focused.

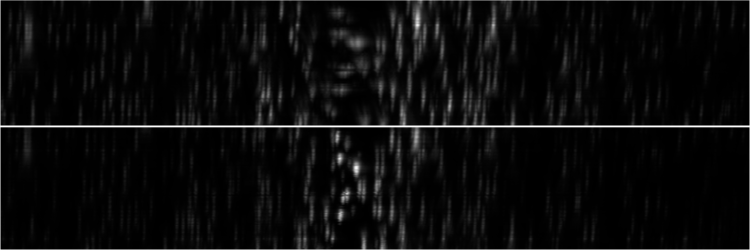
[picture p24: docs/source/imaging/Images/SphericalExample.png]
Before and after of adjusting in Z-projections after adjusting the correction collar


    **Figure 4:** Before and after of adjusting in Z-projections after adjusting the correction collar

-------------

Sample Image Examples
^^^^^^^^^^^^^^^^^^^^^

When imaging samples, it is important to note the way in which the individual images comprising our z-stack might
look as it might differ from what one might traditionally be accustomed to. In our imaging scheme, we essentially
have a thin column of light spanning the vertical direction on our image. This results in each image in the
z-stack being a thin snapshot of the whole sample, which can then be viewed through max intensity projections in
ImageJ. To give a visual reference of what these individual images in a stack can look like for a biological sample, we
provide the following images taken of a mouse embryonic fibroblast sample at a single z-position in a stack for 4
different imaging channels (gold = actin, gray = tubulin, cyan = nuclei, and magenta = Golgi apparatus).

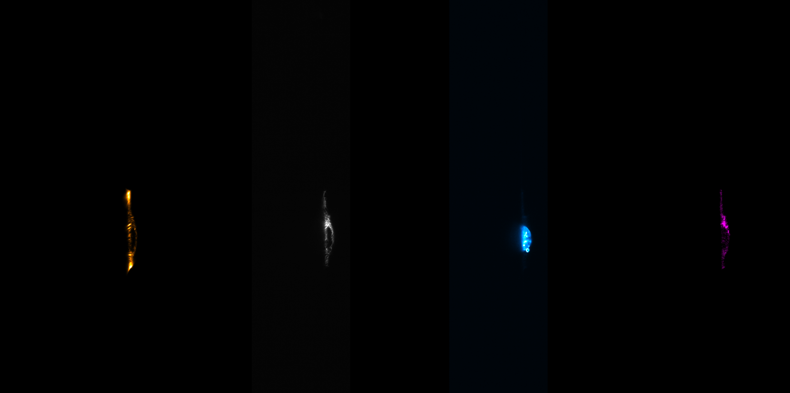
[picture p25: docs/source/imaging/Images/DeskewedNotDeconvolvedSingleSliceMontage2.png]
Example individual images for MEF cells


    **Figure 5:** Example individual images for MEF cells

-------------

Image Stack Processing
______________________

Deskewing
^^^^^^^^^

With an image stack acquired, some post processing is still required in order to remove the effects of shearing in our images. The root of this shearing is due to the angled method in which our sample is mounted and similarly, the angled path that the sample moves as the piezo is scanned. A basic visual idea of how deskewing affects the resulting image is shown below for 100 nm fluorescent beads. Here before deskewing for the same image plane (yz), the beads appear to be stacked in a straight line but oriented along an angle, which is not the most accurate representation of our system. On the deskewed image on the right, one can see that the beads are now properly angled correspond to our piezo angle mount, and that the PSFs of the beads is now correctly aligned along the z axis.

Difference between an image set of 100 nm bead before deskewing (left) and after (right)

    **Figure 6:** Difference between an image set of 100 nm bead before deskewing (left) and after (right)

To do this deskew processing, we utilize custom-built python code via Jupyter notebooks `available here
<https://github.com/TheDeanLab/altair/blob/main/downloads/common/python/Deskewing_1Channel_Compass.ipynb>`_.
The user needs to provide the correct file path to the .tif image stack collected via navigate, as well as the parameters of the imaging system like z-step size, xy pixel size, and the angle that the images should be deskewed over. In our case, our deskew angle is equivalent to 90-60.5 degrees, where 60.5 degrees corresponds to the difference between the normal of our angle mount and the y-axis. If this value is unknown, one can use different values for the deskew angle until the bead PSFs are correctly aligned along the z-axis and not angled.

Reslicing
^^^^^^^^^

Reslicing in ImageJ is a process that allows one to be able to reconstruct different planes of a 3D image set. In other words, it allows one to view the XY, XZ, and YZ projections of the same image set. In our system, our default viewing plane is the XY plane, and so we reslice to observe the XZ and YZ planes. The reslicing process within ImageJ is done after deskewing, and involves opening up the Reslicing panel (Image-> Stacks-> Reslice). Within this panel, one just needs to select the direction of the reslice (typically just top or left). For our system, top slicing provides us with the YZ plane view where one can observe the angled orientation of our sample setup after projection (Image-> Stacks-> Z Project). This is shown below for the same 100 nm bead samples used in the Deskewing and Rescaling portions of this page.

Reslicing Panel for top reslicing

    **Figure 7:** Reslicing Panel for top reslicing

The YZ projection of our bead images after reslicing.

    **Figure 8:** The YZ projection of our bead images after reslicing.

The same process can then be done to obtain the XZ plane view of our sample by reslicing left instead:

Reslicing Panel for left reslicing

    **Figure 9:** Reslicing Panel for left reslicing

The XZ projection of our bead images after reslicing.

    **Figure 10** The XZ projection of our bead images after reslicing.

Deconvolution
^^^^^^^^^^^^^

Deconvolution is an iterative post-processing technique that aims to enhance the resolution of a given image. Typically, in order to properly utilize deconvolution techniques one needs not only to have an image that they want to enhance, but also have an image of the corresponding point-spread-function (PSF) of the system used to take the image. We generate this PSF through taking an image stack of an isolated 100 nm fluorescent bead. For deconvolution we utilize `PetaKit5D <https://github.com/abcucberkeley/PetaKit5D>`_, which is open-source and MATLAB-based image processing code base. It should be noted that deconvolution techniques, while powerful, are also highly dependent on a variety of sensitive input parameters, and finding an effective combination of these parameters can often be a difficult process.

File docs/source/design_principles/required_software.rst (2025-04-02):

.. _software-home:

########
Software
########

The **software for optical simulations and computer-aided design (CAD)** is optional and only required for users who wish to **modify or customize Altair**. However, **navigate is mandatory** for microscope operation unless an alternative **open-source acquisition platform** is used. For **Altair-LSFM**, which operates in a **sample-scanning geometry**, **shearing** is necessary to properly align data spatially; while various software options exist, we provide **Python-based scripts** for this task. Lastly, **deconvolution is optional**, depending on the user’s specific imaging and analysis needs.

.. _optical-simulation-software:

---------------

Optical Simulations
====================

Performing accurate optical simulations is essential for designing and validating the illumination pathway of
**Altair**. To facilitate this process, we used **Zemax OpticStudio (Ansys)** to model the full illumination
system, optimizing the placement of each optical element to achieve the desired focusing and collimation properties.

To replicate or modify these simulations, a **Zemax OpticStudio (Ansys)** professional or academic license is needed.
This enables optical modeling, ray tracing, and tolerance analysis. The **Zemax simulation files** used to design the
Altair illumination system are included in the project’s GitHub repository. These files allow users to inspect and
modify the optical layout, test different lens configurations, and refine performance metrics as needed.

---------------

.. _3d-design:

Computer-Aided Design
=====================

For the design of custom parts and the baseplate, we used **Autodesk Inventor**. Academic licenses for Autodesk
products are available free of charge on their `website <https://www.autodesk.com/education/edu-software/overview?sorting=featured&filters=individual>`_.

To ensure **Autodesk Inventor** correctly locates and manages the CAD files, it is necessary to set up a **new project**
and define the workspace. We recommend following these steps:

Setting Up a New Project in Autodesk Inventor
----------------------------------------------

1. **Launch Autodesk Inventor**
2. Navigate to **File → Manage → Projects**

   

3. When the **Projects** window appears, select **New**

   

4. Choose **New Single User Project**

   

5. **Specify a Project Name** and set the **root directory of the cloned Altair GitHub repository** as the **Project (Workspace) Folder**

   

By configuring Autodesk Inventor in this way, all CAD files associated with **Altair** will be properly linked,
ensuring seamless loading of all components and assemblies.

---------------

.. _microscope-control-software:

Microscope Control Software: navigate
=====================================

To control and operate **Altair**, we use **navigate**, a Python-based software package designed to provide
flexible and intelligent microscope control. **navigate** enables users to interact with the system through
a variety of advanced modalities, including **smart acquisition routines** that dynamically adjust microscope
performance based on the biological specimen.

Features of navigate
--------------------

**navigate** provides key functionalities that enhance the efficiency and adaptability of the Altair system:

- **Automated Smart Acquisition** – Dynamically optimizes imaging parameters in real time, adapting to specimen
  properties to improve image quality.
- **Hardware Abstraction Layer** – Enables seamless control of multiple hardware components, allowing users
  to configure, modify, and expand the microscope's functionality.
- **High-Throughput Data Acquisition** – Facilitates volumetric imaging with high-speed acquisition routines,
  ensuring efficient data collection without compromising spatial or temporal resolution.

Installation and Access
-----------------------

**navigate** is **open-source** and publicly available on GitHub. Installation instructions, along with
comprehensive documentation, can be found here:
`navigate Installation Guide <https://thedeanlab.github.io/navigate/software_installation.html>`_

---------------

Post-Processing
===============

After image acquisition, post-processing is often necessary to extract meaningful biological information.
The **navigate** software package includes libraries for performing **basic image post-processing tasks**,
such as **shearing correction**, which can be applied directly to acquired datasets. We provide Python-based scripts in the
`post_processing` folder of this repository as an example.

Deconvolution
-------------

For more advanced processing, such as **deconvolution**, we recommend using **PetaKit5D**. This software
package is optimized for handling large-scale volumetric datasets and provides state-of-the-art deconvolution
algorithms to enhance image quality and resolution [#]_. **PetaKit5D** must be installed separately and can be found
here: `PetaKit5D GitHub Repository <https://github.com/abcucberkeley/PetaKit5D>`_

.. rubric:: Citations

.. [#] Ruan X, Mueller M, Liu G, Görlitz F, Fu TM, Milkie DE, Lillvis JL, Kuhn A, Gan Chong J, Hong JL,
   Herr CYA, Hercule W, Nienhaus M, Killilea AN, Betzig E, Upadhyayula S. *Image processing tools for
   petabyte-scale light sheet microscopy data.* **Nat Methods.** 2024 Dec;21(12):2342-2352.
   doi: `10.1038/s41592-024-02475-4 <https://doi.org/10.1038/s41592-024-02475-4>`_.
   PMID: `39420143 <https://pubmed.ncbi.nlm.nih.gov/39420143/>`_, PMCID: PMC11621031.

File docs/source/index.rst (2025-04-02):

.. _altair-home:

#####################
**Altair**
#####################

Biologists are increasingly transitioning towards more complex assays that require volumetric imaging with high spatiotemporal resolution. Whether it is a developing embryo, the formation of an immunological synapse, cancer migrating through a 3D collagen matrix, these biological processes can only be understood when non-invasively and quantitatively evaluated in their entirety through time.

To meet these growing demands, we aim to develop simplified optical systems that provide cutting-edge imaging performance while ensuring ease of assembly and accessibility. By leveraging precision-engineered, baseplate-mounted designs, we eliminate unnecessary degrees of freedom, making high-resolution light-sheet microscopy more robust, reproducible, and approachable for researchers across disciplines. Our goal is to create powerful yet modular imaging platforms that enable biologists to focus on discovery rather than instrument complexity, accelerating the adoption of advanced volumetric imaging techniques.

-----------

**Project Philosophy**
=========================

- **High-performance, easy-to-assemble light-sheet microscopes** designed for broad accessibility.
- **Seamless integration** with **navigate** software for optimized operation and intelligent imaging workflows.
- **Precision-engineered optomechanical design** for ease of use, reproducibility, and low maintenance.
- **Streamlined optoelectronics and control architecture** for robust, reliable, and modular system operation.
- **Modular, adaptable platforms** that support future advancements in light-sheet microscopy.

--------

.. warning::

    Please be advised that while the Dean Lab has implemented several safeguards,
    there are inherent risks associated with the use of such
    mechanical and optical systems. Despite these precautions, the complexity and nature of
    hardware can lead to unpredictable outcomes. Therefore, the Dean Lab and UT
    Southwestern expressly disclaim any responsibility for any damages, losses, or
    injuries that may arise from or be related to the use of **Altair**.
    Users should be aware of these risks and agree to utilize **Altair** at their own risk.

.. warning::

    **Licensing Note:** These design materials are freely available to academic and non-profit users for research and educational purposes. Commercial or for-profit entities must obtain a license before use; please contact the `Office of Technology Development <https://www.utsouthwestern.edu/about-us/administrative-offices/technology-development/>`_ for more information.

--------

.. toctree::
   :caption: Table of Contents
   :maxdepth: 2

   introduction/introduction
   introduction/background
   design_principles/required_software
   hardware/index.rst
   design_principles/design_process
   physical_assembly/physical_assembly
   system_characterization/system_characterization
   imaging/imaging
   future/index

**Authors**
============
Dr. John Haug performed all simulations, design, testing, and validation of Altair. Seweryn Gałecki provided
cells for testing imaging performance and assisted in their visualization. Dr. Kevin Dean oversaw and provided feedback on all research operations. This project also benefited from valuable feedback from the **Dean, Fiolka, and Danuser labs** at **UTSW**.

**Acknowledgements**
====================
The authors extend their gratitude to Calvin Jones and `Dr. Sophia Theodossiou <https://www.boisestate.edu/coen-mbe/directory/sophia-theodossiou/>`_ (Boise State University) for
their assistance in designing and printing the custom sample chamber, as well as **Melissa Glidewell** for her
initial evaluation of optical tolerances.

**Funding**
============
**navigate** is supported by the
`UT Southwestern and University of North Carolina Center for Cell Signaling
<https://cellularsignaltransduction.org>`_, a Biomedical Technology Development and Dissemination (BTDD) Center funded by the NIH National Institute of General Medical Science (RM1GM145399), and the `Center for Metastatic Tumor Imaging <https://www.metastasis-imaging.org>`_ program, a Cellular Cancer Biology Imaging Research (CCBIR) program funded by the NIH National Cancer Institute (U54CA268072).

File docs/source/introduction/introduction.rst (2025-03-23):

============
Introduction
============

.. _volumetric-imaging:

Why is Volumetric Imaging Important?
====================================

Biological processes occur in a fundamentally three-dimensional (3D) space, and the spatial organization of
molecular structures is critical to cellular function. Traditional two-dimensional (2D) imaging provides only
a limited cross-section of these dynamic events, often obscuring key interactions and leading to incomplete
or misleading interpretations.

For instance, during mitosis, chromosomes undergo intricate rotations within the entire cellular volume,
and microtubules dynamically polymerize and depolymerize as they engage and separate daughter
chromosomes at their kinetochores. In 2D imaging, these structures inevitably drift in and out of the focal
plane, making it challenging to track such dynamic processes over time. Similarly, in complex tissue
environments, organelle positioning, cell-cell interactions, and subcellular signaling pathways are all
inherently shaped by their 3D spatial context.

By capturing the full volume of a specimen, volumetric imaging enables a more accurate representation of
cellular architecture and dynamic molecular events. This is particularly critical for understanding
developmental biology, disease progression, and cellular interactions within their native environments.
Emerging technologies such as light-sheet microscopy, expansion microscopy, and advanced computational
imaging now allow researchers to visualize biological systems at unprecedented resolutions, bridging the
gap between molecular detail and tissue-scale organization.

---------------

.. _why-light-sheet:

The Importance of Parallelization
=================================

Historically, 3D imaging has been performed using spinning disk and laser scanning
confocal microscopes. However, these microscopes waste significant excitation
energy on out-of-focus regions, leading to unnecessary photodamage while requiring
compensatory increases in laser power due to their low illumination duty cycle. This problem
is further exacerbated by their sequential, point-by-point image acquisition, which limits
speed and increases photobleaching.

.. sidebar:: **Illumination Confinement**
   :class: sidebar-note

   **Illumination confinement** refers to the restriction of excitation light to within the **depth of focus** of the
   detection objective, ensuring that only light contributing to image formation is used. This is a key advantage of
   **light-sheet fluorescence microscopy (LSFM)**, where the illumination plane is matched to the detection plane,
   minimizing out-of-focus excitation and reducing phototoxicity.

In contrast, depending on their design, light-sheet fluorescence microscopes (LSFM)
restrict illumination primarily to the focal plane of interest, minimizing phototoxicity while
maximizing imaging efficiency. Additionally, by leveraging highly sensitive scientific cameras
(e.g., 4×10\ :sup:`6` pixels), LSFM enables massively parallelized image acquisition—recording
entire planes in a single exposure rather than scanning point-by-point.

For instance, a typical laser scanning confocal microscope requires **~4.16s** to acquire
a **2048 × 2048** voxel image, given a voxel dwell time of **1µs**. In contrast, an LSFM can
image the same region in just **~5ms**, an **832-fold** increase in speed, all while maintaining a
**5,000-fold longer** per-voxel dwell time. This extended dwell time enables improved signal
accumulation, lower laser power requirements, and a significantly improved signal-to-noise
ratio (SNR). As a result, LSFM is uniquely suited for long-term volumetric imaging at high
spatiotemporal resolution while reducing photodamage.

.. sidebar:: **Spatial Duty Cycle**
   :class: sidebar-note

   The **spatial duty cycle of illumination** refers to the fraction of a sample that is actively contributing to
   image formation at any given moment during an imaging process. In **laser scanning confocal microscopy**,
   only a single point is illuminated at a time, resulting in a **low duty cycle** and requiring compensatory increases in laser
   power to maintain signal. In contrast, **light-sheet fluorescence microscopy (LSFM)** illuminates and images an entire plane at once,
   yielding a **duty cycle** that approaches 100%, enabling drastically reduced laser powers that reduce phototoxicity, .

---------------

.. _challenges:

Challenges with 3D Imaging
==========================

To extract meaningful biological insight from volumetric imaging, microscopes must achieve
sufficient **spatiotemporal resolution** while preserving molecular specificity and compatibility with advanced
analytical techniques. This requires integration with biosensors, opto- and chemogenetic tools, and
computer vision analyses that translate **high-dimensional 5D datasets** (x, y, z, :math:`\lambda`, t) into
quantitative biological readouts. Several key challenges must be addressed to ensure the accuracy and
reliability of 3D imaging:

-   **Nyquist Sampling in Space and Time:**
    To faithfully capture dynamic processes, the event of interest must be **Nyquist sampled** in both
    spatial and temporal dimensions. For example, the GTPase cycle times of Rho, Rac, and Cdc42 can be
    as short as 5s, necessitating volumetric acquisitions at :math:`\leq` 2.5s per volume with a spatial resolution
    of **<500nm**. Furthermore, resolution should ideally be **isotropic or nearly isotropic** to prevent
    morphology-dependent intensity artifacts—particularly for signaling events at the plasma membrane.

-   **Multicolor Excitation and Detection:**
    To enable multiplexed cellular readouts, the microscope must support **simultaneous multicolor imaging**
    with achromatic performance across excitation and detection wavelengths. Microscope designs that
    rely on spatial light modulators (SLMs) for excitation often struggle to achieve this, as the diffraction
    efficiency of SLMs varies with wavelength.

-   **Detection Sensitivity and Phototoxicity:**
    Imaging performance must be **photon-efficient** to minimize the need for high ectopic expression of
    signaling-active proteins and to mitigate **photobleaching and phototoxicity**—a challenge that
    is amplified when acquiring **10–100 slices per volume**. Maximizing quantum efficiency and minimizing
    out-of-focus excitation are crucial for maintaining live-cell viability.

-   **Field of View Constraints:**
    When imaging dynamic processes in **extracellular matrix environments** (where cells can migrate in
    any direction) or within a **developing embryo**, the microscope must provide a sufficiently **large field
    of view (FOV)**—ideally **>100 × 100 × 100 µm**. Many leading **light-sheet fluorescence microscopes
    (LSFMs)** are optimized for small fields of view (e.g., 25µm), which limits their applicability to studies
    of large-scale tissue dynamics.

-   **Avoidance of Computational Post-Processing Biases:**
    To ensure compatibility with **quantitative downstream analyses**, reliance on iterative **deconvolution**
    or structured illumination routines should be minimized. These techniques can introduce statistical
    artifacts that distort numerical analyses, particularly when measuring intensity distributions, localization
    precision, or dynamic molecular interactions.

.. sidebar:: **Nyquist Sampling**
   :class: sidebar-note

   **Nyquist sampling** is a fundamental principle in signal processing that dictates the minimum sampling
   frequency required to accurately reconstruct a signal without aliasing. According to the **Nyquist-Shannon
   sampling theorem**, a continuous signal must be sampled at least **twice the highest frequency component**
   present in the signal to ensure faithful reconstruction.

   In microscopy, Nyquist sampling applies to both **spatial and temporal domains**:

   - **Spatial Nyquist Sampling:** To accurately resolve features of size :math:`d`, the sampling interval
     (pixel or voxel spacing) should be no greater than :math:`d/2`. This ensures that high-frequency
     structural details are captured without loss of information.

   - **Temporal Nyquist Sampling:** To track dynamic processes occurring at a characteristic frequency
     :math:`f_c`, images must be acquired at a frequency of :math:`\geq 2 \times f_c` to prevent
     aliasing in time-lapse imaging.

   Failure to meet the Nyquist criterion results in **aliasing**, where high-frequency components are misrepresented
   as lower-frequency artifacts, distorting biological measurements.

Meeting these criteria is essential for **accurate, high-throughput volumetric imaging** that captures
cellular dynamics with sufficient fidelity to support rigorous biological interpretation.

---------------

.. _why-build:

Why Build a Microscope?
========================

The technology required to achieve **multiplexed volumetric imaging** with advanced probes and computer vision
analyses already exists. However, the commercialization process imposes significant constraints on innovation.
Microscope manufacturers prioritize **aesthetically attractive, highly engineered, and serviceable optical
systems** that ensure a large return on investment. As a result, they tend to be **extremely conservative** in
adopting emerging technologies.

Most commercially available microscopes take **over seven years** to develop, by which time they are often
already obsolete due to rapid scientific advancements. A notable exception is the **Lattice Light-Sheet Microscope
(LLSM)**, which was sublicensed by Zeiss to 3i shortly after its seminal publication. However, even in this case,
it took another **six years** for Zeiss to release a consumer-friendly model—at a prohibitive cost of **~$1M USD**.

Beyond commercialization delays, **patent restrictions** further stifle innovation. The **highly fragmented and
entangled intellectual property (IP) landscape** makes it difficult for new start-ups to enter the market. For
example, despite their own **limited role in developing oblique plane microscopy (OPM)**, Leica has exclusively
licensed a patent for **off-axis tertiary imaging systems**, effectively blocking broader commercialization of OPM.

As a result, reliance on commercial microscope development not only **delays technology adoption** but can
actively **impede the dissemination of transformative imaging methods**. This reality makes in-house development
of custom microscopy platforms essential for pushing the frontiers of biological imaging forward.

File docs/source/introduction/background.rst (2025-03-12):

###########################################################
Overview of Subcellular Light-Sheet Microscope Technologies
###########################################################

Light-sheet fluorescence microscopy (LSFM) has undergone significant advancements, leading to the development of specialized approaches tailored for **subcellular-resolution imaging**. These methods balance **resolution, field of view, optical sectioning, and phototoxicity** to accommodate different biological applications. Below, we provide an overview of existing high-resolution light-sheet microscope technologies, their strengths, and their limitations.

-----------------------

Lattice Light-Sheet Microscopy (LLSM)
-------------------------------------

Lattice Light-Sheet Microscopy (LLSM) employs a **superposition of propagation-invariant beams** to generate a structured light-sheet that theoretically maintains a **narrow beam waist** over extended distances. However, in practice, these beams introduce **sidelobes** that increase with beam length, contributing to **out-of-focus blur** and degrading image contrast and resolution. As a result, LLSM is most effective for **small fields of view (~25µm)**, making it ideal for imaging **adherent cells and epithelial monolayers**.

A key limitation of LLSM is its reliance on a **spatial light modulator (SLM)** to sculpt its illumination beams. While this enables fine control over the excitation profile, it also introduces significant drawbacks:
- **Limited Multicolor Excitation** – The SLM prevents simultaneous multicolor excitation, making LLSM suboptimal for **multiplexed biosensor imaging**.
- **Reduced Light Throughput** – The optical train has an efficiency of only **~2.4%**, requiring higher-power and more expensive laser sources.
- **Increased Complexity** – The integration of an SLM significantly increases the complexity and cost of the system, limiting accessibility.

-----------------------

Field Synthesis
---------------

To address the limitations of Lattice Light-Sheet Microscopy (LLSM), the Fiolka lab developed
**Field Synthesis**, a mathematical framework that reconstructs **time-averaged (dithered) lattice light-sheets**
using **diffractive optics**. Unlike LLSM, which requires a **spatial light modulator (SLM)** to project complex
amplitude and phase patterns onto the illumination objective, **Field Synthesis achieves the same illumination
effect with greater light throughput and full compatibility with simultaneous multicolor excitation**.

Instead of directly sculpting the beam at the objective’s pupil, Field Synthesis employs a **focused line scan
over a binary pupil mask using a galvanometer during a single camera exposure**. This approach requires only:

- **A galvanometer for beam scanning**
- **A binary phase mask to shape the illumination**
- **A 4f telescope for beam relay**

Because of this design, **Field Synthesis provides resolution and photobleaching characteristics statistically
indistinguishable from LLSM** while offering **2× higher acquisition speeds** in simultaneous multicolor imaging.
For example, in a **sample-scanning configuration**, Field Synthesis was used to capture high-resolution,
simultaneous imaging of **PI3K activity and dynamic filopodia and bleb formation** in **MV3 melanoma cells**.
The increased imaging speed significantly reduced **motion blur**, which is particularly beneficial for visualizing
rapid morphological transitions such as **filopodial buckling**.

-----------------------

Dual Inverted Selective Plane Illumination Microscopy (diSPIM)
---------------------------------------------------------------

**Dual Inverted Selective Plane Illumination Microscopy (diSPIM)** is a commercially available light-sheet system that utilizes **two opposing objectives** to achieve isotropic resolution through sequential orthogonal illumination and detection. Unlike conventional LSFM, where a single objective delivers the light-sheet and another detects fluorescence, diSPIM alternates between two objectives, each serving both roles in successive acquisitions. This configuration enables **volumetric imaging with improved axial resolution**, as images from both orientations can be fused computationally to reconstruct a high-fidelity 3D volume. While diSPIM is **well-suited for live-cell imaging**, its reliance on sequential acquisition leads to **lower temporal resolution** compared to single-objective LSFM approaches. Additionally, alignment complexity and computational post-processing requirements can introduce challenges, particularly for rapid dynamic events. Despite these limitations, diSPIM remains a **flexible and widely adopted platform**, particularly in studies requiring high-resolution imaging of small organisms, embryos, and adherent cells.

Axially Swept Light-Sheet Microscopy (ASLM)
-------------------------------------------

Axially Swept Light-Sheet Microscopy (ASLM) overcomes many of the optical constraints of traditional light-sheet imaging by implementing a **rapidly scanned Gaussian beam** to create an extended, ultra-thin light-sheet. Unlike LLSM, ASLM minimizes **sidelobe artifacts**, resulting in superior **optical sectioning and contrast** across a larger field of view. Key advantages of ASLM include:
- **Diffraction-Limited Isotropic Resolution** – Achieves **300–400 nm** axial resolution while maintaining high lateral resolution.
- **Improved Optical Sectioning** – Reduces out-of-focus excitation, enhancing signal-to-noise ratios.
- **Compatibility with Multicolor Imaging** – Unlike LLSM, ASLM does not require an SLM, allowing for **simultaneous multicolor excitation**, essential for biosensor applications.

However, ASLM is inherently **slower than conventional light-sheet methods**, as the sweeping mechanism imposes limits on acquisition speed. Additionally, its implementation requires precise **synchronization between beam scanning and camera acquisition**, adding some complexity to its control systems.

-----------------------

Oblique Plane Microscopy (OPM)
------------------------------

The orthogonal illumination and detection geometry used in most **light-sheet fluorescence microscopes (LSFMs)**
comes with several **underappreciated limitations**. This configuration is **incompatible** with many standard
laboratory imaging setups, including **hardware-based autofocus systems** that mitigate thermal and mechanical drift,
**standard imaging dishes**, **multi-well plates**, and **microfluidic devices** designed for establishing **chemotactic
gradients** or delivering **controlled shear stress** in parallel plate flow chambers.

Additionally, LSFMs often require **large imaging chambers** (e.g., **~8.5 mL** for **LLSM**), leading to **high reagent
consumption**, which can be cost-prohibitive for experiments involving **chemogenetic or pharmacological perturbations**.
The use of **high numerical aperture (NA) water-dipping objectives** further **compromises sterility**, making
long-term imaging of slow biological processes, such as **sarcomerogenesis over ~24 hours**, particularly challenging.

Although ultra-thin **fluorocarbon foil-based cuvettes** have been explored as a solution, even slight **refractive
index mismatches** introduce **spherical aberrations**, degrading image resolution and sensitivity. These factors
highlight the need for alternative light-sheet implementations that maintain **high optical performance while
accommodating diverse experimental conditions**.

Oblique Plane Microscopy (OPM) represents a **single-objective light-sheet imaging approach** that overcomes these challenges. Here, owing to its unique non-coaxial design, an obliquely launched illumination beam is used to achieve volumetric imaging without requiring an orthogonally positioned objective. This method has gained popularity for **live-cell imaging** due to its advantages:
- **Simplified Geometry** – Requires only a single high-NA objective, making it more compact and easier to integrate into existing microscope setups.
- **High-Speed Volumetric Imaging** – Can acquire full 3D volumes at video rate.
- **Compatible with Conventional Sample Mounting** – Unlike traditional LSFM, OPM does not require complex sample positioning or embedding techniques.

Despite its advantages, OPM suffers from **anisotropic resolution** and often requires **computational post-processing** (e.g., shearing correction) to reconstruct datasets accurately. Additionally, due to the oblique illumination geometry, axial resolution may degrade deeper into the sample.

-----------------------

+------------------------------+----------------------------------------------------+--------------------------------------------------+
| **Microscope Type**          | **Strengths**                                      | **Limitations**                                  |
+------------------------------+----------------------------------------------------+--------------------------------------------------+
| **LLSM**                     | - High-resolution for small samples                | - Limited field of view (~25µm)                  |
|                              | - Excellent optical sectioning                     | - Incompatible with multicolor excitation        |
|                              |                                                    | - Low light throughput (~2.4%)                   |
|                              |                                                    | - Requires high-power lasers                     |
+------------------------------+----------------------------------------------------+--------------------------------------------------+
| **Field Synthesis**          | - Statistically indistinguishable from LLSM        | - Requires scanning with a galvanometer          |
|                              | - Higher light throughput                          | - Less widely implemented than LLSM              |
|                              | - Compatible with simultaneous multicolor imaging  | - Slightly lower spatial control than LLSM       |
|                              | - Faster acquisition (~2× speed vs. LLSM)          |                                                  |
+------------------------------+----------------------------------------------------+--------------------------------------------------+
| **diSPIM**                   | - Dual-objective design improves axial resolution  | - Multiple volumes must be acquired              |
|                              | - Enables isotropic volumetric imaging via fusion  | - Requires post-processing for image fusion      |
|                              | - Well-suited for live-cell and embryo imaging     | - Greater alignment complexity                   |
|                              | - Commercially available and widely adopted        |                                                  |
+------------------------------+----------------------------------------------------+--------------------------------------------------+
| **ASLM**                     | - High contrast and improved optical sectioning    | - Lower acquisition speed due to beam sweeping   |
|                              | - Isotropic resolution (~300–400 nm)               | - Requires precise synchronization               |
|                              | - Compatible with multicolor imaging               | - Complex scanning mechanics                     |
+------------------------------+----------------------------------------------------+--------------------------------------------------+
| **OPM**                      | - Single-objective system (simplified geometry)    | - Anisotropic resolution                         |
|                              | - High-speed volumetric imaging                    | - Requires computational post-processing         |
|                              | - Compatible with conventional sample mounting     | - Axial resolution degrades with depth           |
+------------------------------+----------------------------------------------------+--------------------------------------------------+

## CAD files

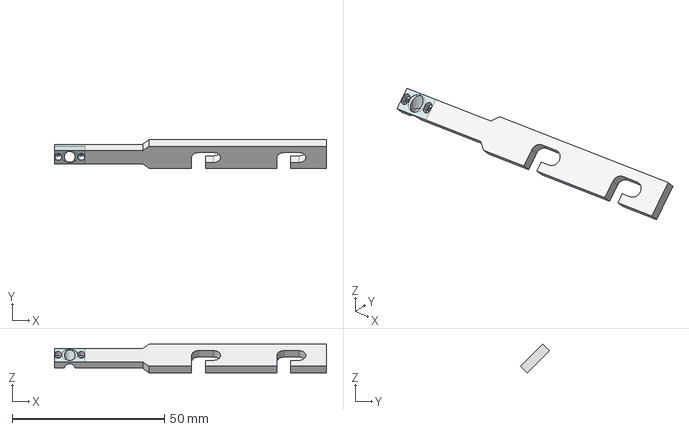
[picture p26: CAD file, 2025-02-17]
downloads/common/cad/SampleHolder_Main.stp
89.2 x 9.39 x 9.39 mm

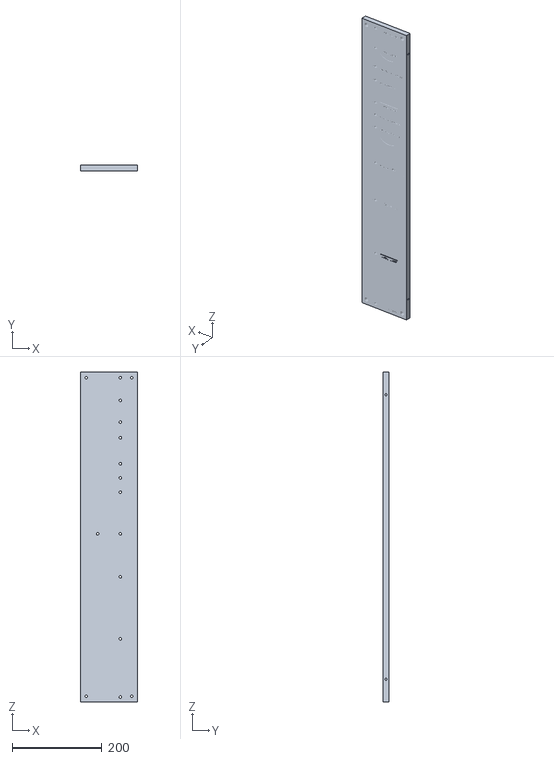
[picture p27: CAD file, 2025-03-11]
downloads/base/cad/COMPASS_Baseplate_base.stl
127.0 x 12.7 x 736.6

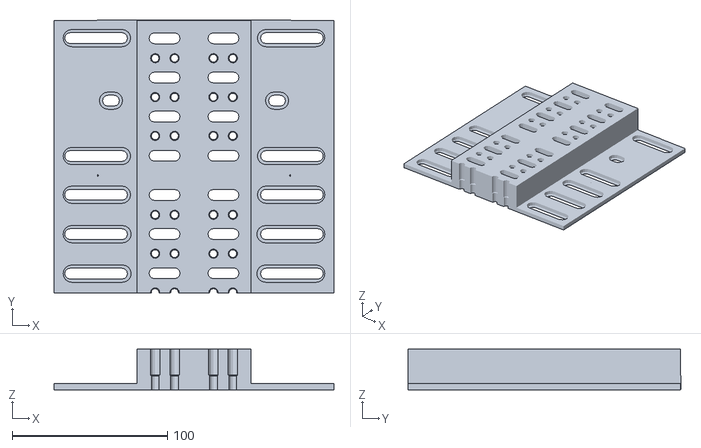
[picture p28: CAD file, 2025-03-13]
downloads/common/cad/TranslationStagetoBreadboardAdapter_Baseplate.stl
180.2 x 175.6 x 26.2

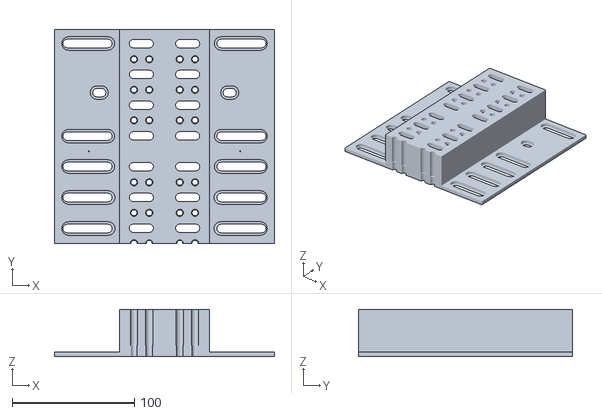
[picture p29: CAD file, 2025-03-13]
downloads/common/cad/TranslationStagetoBreadboardAdapter_NoBaseplate.stl
180.2 x 175.6 x 38.9

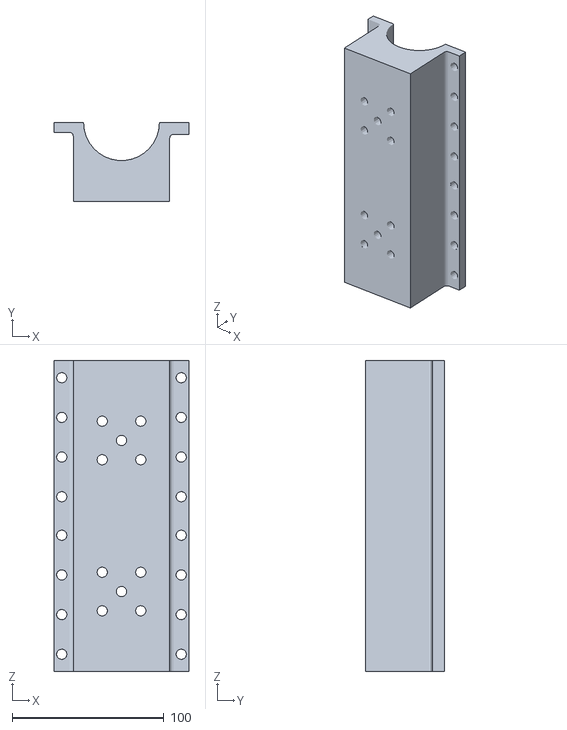
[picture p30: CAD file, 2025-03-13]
downloads/common/cad/TranslationStageTubeLensAdapter.stl
88.9 x 51.7 x 205.0

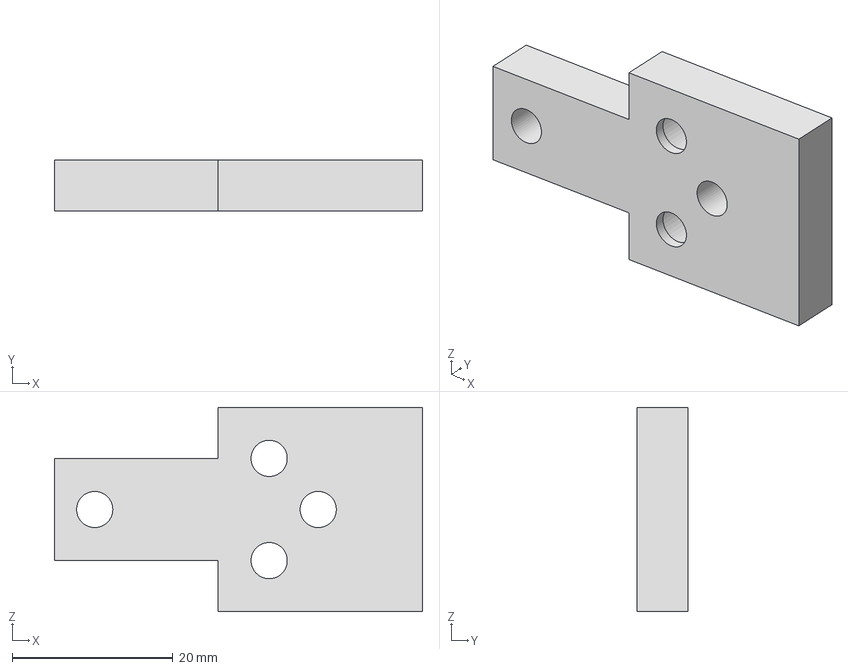
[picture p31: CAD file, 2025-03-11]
downloads/common/cad/SampleHolderToKB1X1TMagneticHolder.stp
45.7 x 6.35 x 25.4 mm

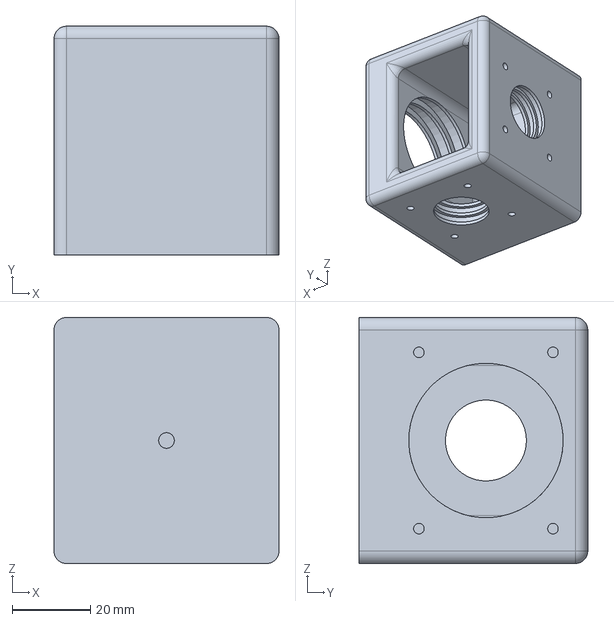
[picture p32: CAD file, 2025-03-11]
downloads/common/cad/SampleChamber.stp
57.4 x 58.4 x 62.8 mm

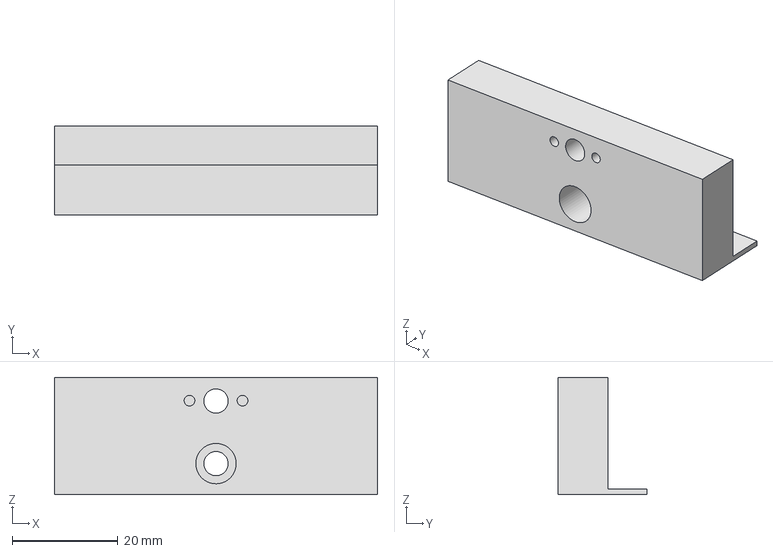
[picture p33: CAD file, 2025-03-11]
downloads/common/cad/VA100CPtoPolarisAdapter.stp
61.0 x 16.8 x 22.1 mm

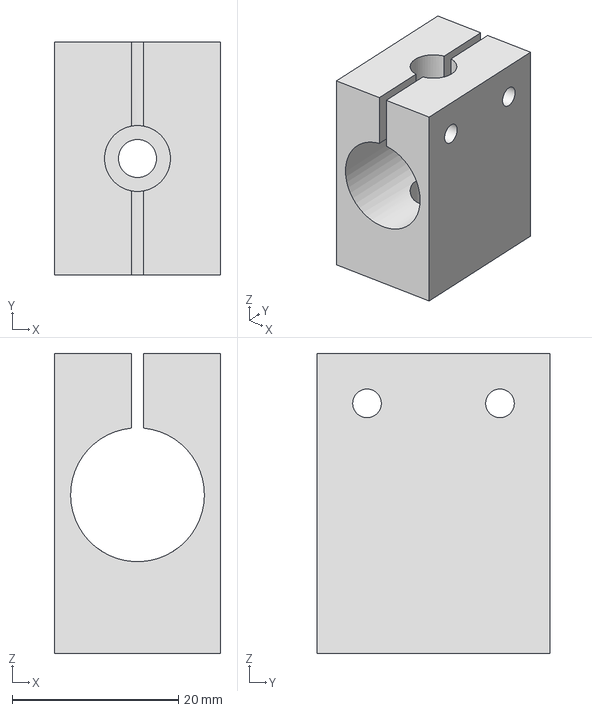
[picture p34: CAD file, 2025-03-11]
downloads/common/cad/GalvoHoldertoPolarisMount.stp
20.0 x 28.0 x 36.1 mm

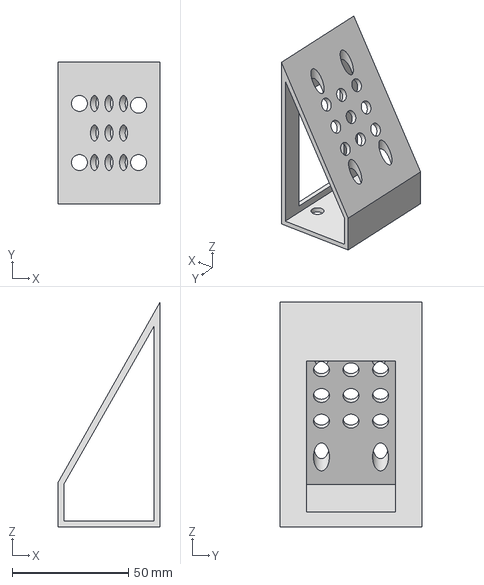
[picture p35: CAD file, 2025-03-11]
downloads/common/cad/AngleMount.stp
43.9 x 61.0 x 96.7 mm

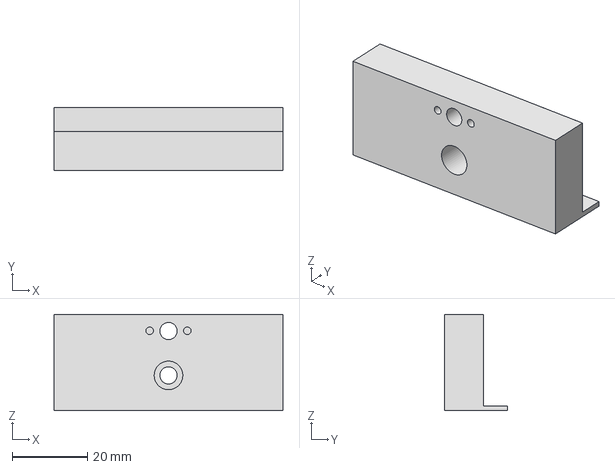
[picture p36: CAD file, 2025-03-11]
downloads/common/cad/RSP1toPolarisPinAdapter.stp
61.0 x 16.8 x 25.6 mm

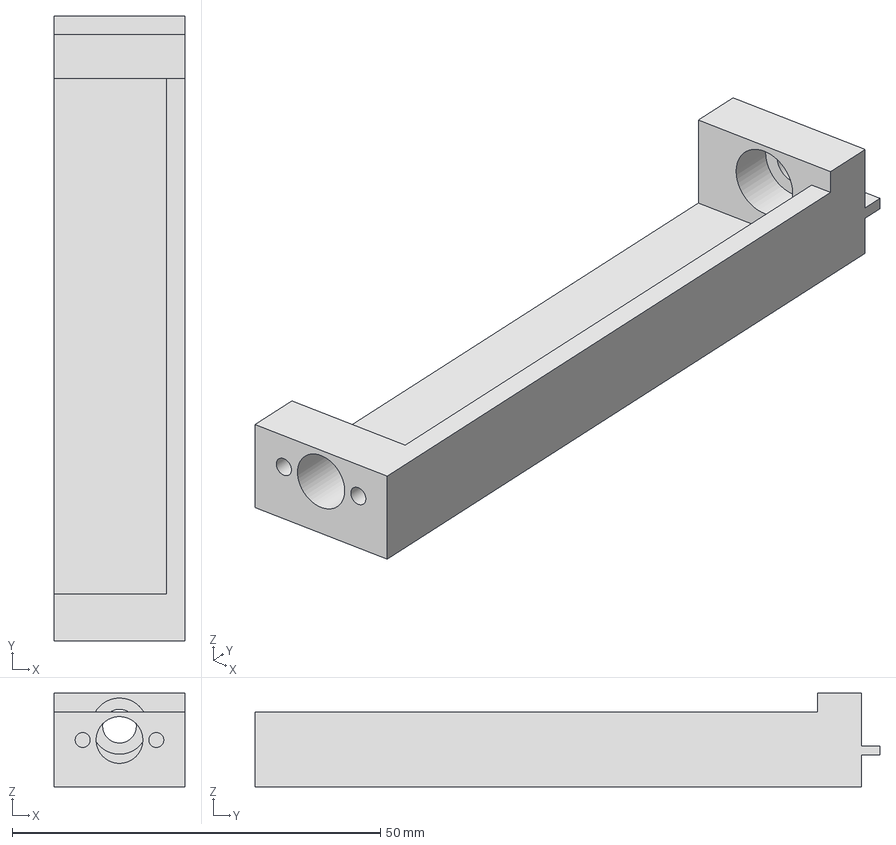
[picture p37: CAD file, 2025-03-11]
downloads/common/cad/IDA12toPolarisAdapter.stp
17.8 x 84.8 x 12.7 mm

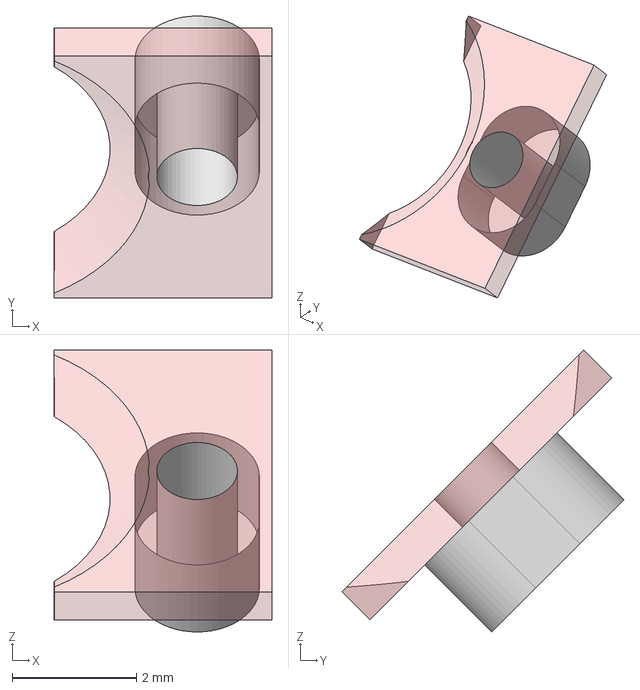
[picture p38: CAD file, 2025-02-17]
downloads/common/cad/SampleHolder_Clamp.stp
3.50 x 4.53 x 4.53 mm

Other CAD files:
downloads/base/cad/COMPASS_Baseplate_base.ipt
downloads/common/cad/AngleMount.ipt
downloads/common/cad/AngleMount.stl
downloads/common/cad/GalvoHoldertoPolarisMount.ipt
downloads/common/cad/GalvoHoldertoPolarisMount.stl
downloads/common/cad/IDA12toPolarisAdapter.ipt
downloads/common/cad/IDA12toPolarisAdapter.stl
downloads/common/cad/RSP1toPolarisPinAdapter.ipt
downloads/common/cad/RSP1toPolarisPinAdapter.stl
downloads/common/cad/SampleChamber.ipt
downloads/common/cad/SampleChamber.stl
downloads/common/cad/SampleHolderToKB1X1TMagneticHolder.ipt
downloads/common/cad/SampleHolderToKB1X1TMagneticHolder.stl
downloads/common/cad/SampleHolder_Clamp.dwg
downloads/common/cad/SampleHolder_Clamp.ipt
downloads/common/cad/SampleHolder_Main.ipt
downloads/common/cad/TranslationStageTubeLensAdapter.ipt
downloads/common/cad/TranslationStagetoBreadboardAdapter_Baseplate.ipt
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

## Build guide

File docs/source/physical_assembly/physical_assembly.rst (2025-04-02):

.. _assembly-home:

###################
Microscope Assembly
###################

---------------

Parts List and Cost
___________________

A breakdown of all components used in Altair, and the approximate cost are included in the collapsable sections below:

.. collapse:: Illumination Path

    .. list-table::
       :header-rows: 1

       * - Standard Parts
         - Vendor
         - Purpose
       * - TL20X-MPL
         - Thorlabs
         - Illumination Objective
       * - Polaris-1XY
         - Thorlabs
         - Mounting
       * - Polaris-K1XY
         - Thorlabs
         - Mounting
       * - Polaris-MA45
         - Thorlabs
         - Mirror Mounting
       * - Polaris-P150
         - Thorlabs
         - Mounting
       * - Polaris-P200
         - Thorlabs
         - Mounting for L4
       * - Polaris-P3
         - Thorlabs
         - Mounting
       * - Polaris-P250
         - Thorlabs
         - Mounting
       * - Polaris-P225
         - Thorlabs
         - Mounting
       * - Polaris-P075
         - Thorlabs
         - Mounting
       * - Polaris-P175
         - Thorlabs
         - Mounting
       * - Polaris-B1S
         - Thorlabs
         - Lens Mounting
       * - Polaris-K1S4
         - Thorlabs
         - Mirror Mounting
       * - CFC11A-A
         - Thorlabs
         - Fiber Laser Collimator
       * - P3-405B-FC-1
         - Thorlabs
         - Single Mode Fiber
       * - AC254-080-A-ML
         - Thorlabs
         - L2
       * - AC254-030-A-ML
         - Thorlabs
         - L1
       * - VA100CP
         - Thorlabs
         - Rectangular Aperture
       * - ACY254-075-A
         - Thorlabs
         - L3
       * - PF10-03-P01
         - Thorlabs
         - 1\" Mirror
       * - RSP1
         - Thorlabs
         - Rotation Mount For Cylindrical Lens
       * - AC254-250-A-ML
         - Thorlabs
         - L4
       * - SM1A12
         - Thorlabs
         - Illumination Objective Mounting
       * - 1-Axis 4kHz Resonant Galvo and Servo
         - Novanta
         - Galvo Mirror
       * - TGPOW-12-3
         - ASI
         - Galvo Low Noise Power Supply +12V 3A
       * - Polaris B1F
         - Thorlabs
         - Mount for Mirror 2
       * - ID12
         - Thorlabs
         - Mounted Circular Iris (12 mm Max Aperture)
       * - L4CC
         - Oxxius
         - Multicolor Laser Source
       * -
         -
         -
       * - **Custom Machined Parts**
         - **Vendor**
         - **Purpose**
       * - RSP1 Polaris Adapter
         - Xometry
         - Polaris Adapter for RSP1 Cylindrical Lens
       * - Illumination Baseplate
         - Xometry
         - Baseplate
       * - Galvo Holder
         - Protolabs
         - Galvo Mounting
       * - VA100CP Polaris Adapter
         - Xometry
         - Aperture Mounting
       * - IDA12 Polaris Adapter
         - Xometry
         - Polaris Adapter for ID12 Iris

.. collapse:: Detection Path

    .. list-table::
       :header-rows: 1

       * - **Part**
         - **Vendor**
         - **Purpose**
       * - N25X-APO-MP
         - Thorlabs (Nikon)
         - Detection Objective
       * - LS-100-AMCCH
         - ASI
         - 100 mm Linear Focusing Stage
       * - TGDCM2
         - ASI
         - 2-Axis Stage Control Card
       * - C60-EXT-15
         - ASI
         - 15 mm Tube Extension
       * - RAO-0051
         - ASI
         - M32x0.75 Threaded Sleeve
       * - FW-0002-8
         - ASI
         - 8-Position Filter Wheel
       * - FW-C-MNT-K1
         - ASI
         - Filter Wheel to MIM Adapter Kit
       * - TGFW
         - ASI
         - Filter Wheel Control Card
       * - C60-TUBE-400
         - ASI
         - 400 mm Achromatic Tube Lens
       * - C13440-20CU
         - Hamamatsu
         - ORCA Flash4.0 V3 Camera
       * - Semrock Brightline Filter 605/15-25nm
         - IDEX
         - Filter
       * - Semrock Brightline Filter 445/20nm
         - IDEX
         - Filter
       * - Semrock Brightline Filter 676/29 nm
         - IDEX
         - Filter
       * - Semrock Brightline Filter 529/24-25nm
         - IDEX
         - Filter

.. collapse:: Sample Positioning

    .. list-table::
       :header-rows: 1

       * - **Part**
         - **Vendor**
         - **Purpose**
       * - KBT1X1T
         - Thorlabs
         - Magnetic Mount for Sample Holder Top
       * - KBB1X1
         - Thorlabs
         - Magnetic Mount for Sample Holder Bottom
       * - LS-5012
         - ASI
         - Breadboard Adapter for Translation Stages
       * - LS-5013
         - ASI
         - Right Angle Bracket for Translation Stages
       * - DV-6010-C
         - ASI
         - Dovetail Mount Pair
       * - LS-50-AMCLLS
         - ASI
         - 50 mm Linear Stage with Stainless Steel Slide
       * - LS-100-AMERL
         - ASI
         - 100 mm Linear Stage, 16 TPI, Extended, Right
       * - LS-50-AMELL
         - ASI
         - 50 mm Linear Stage
       * - TGADEPT
         - ASI
         - Piezo Control Card
       * - HS1.100
         - PiezoConcept
         - 100 Micron Piezo Stage
       * - ADAPTHS1BB
         - PiezoConcept
         - Adapter Plate for PiezoConcept HS1
       * -
         -
         -
       * - **Custom Machined Parts**
         - **Vendor**
         - **Purpose**
       * - Angle Bracket Adapter
         - Xometry
         - Mounting the piezo to ASI translation stages at an angle
       * - 5mm Coverslip Holder
         - Xometry
         - Sample holder for 5 mm Coverslips
       * - 5mm Coverslip Holder Adapter
         - Xomtery
         - Adapter to mount coverslip holder onto KBT1X1T linearly

.. collapse:: Shared Equipment

    .. list-table::
       :header-rows: 1

       * - **Part**
         - **Vendor**
         - **Purpose**
       * - TG16-BASIC
         - ASI
         - Tiger Controller - 16 Bay System
       * - T3283
         - Thorlabs
         - BNC Adapter (F-F)
       * - PAA272R
         - Thorlabs
         - SMB F to BNC M cable adapter
       * - CA2106
         - Thorlabs
         - BNC to Terminal Pin Cable
       * - PCIe-6738
         - NI
         - Data Acquisition Card
       * - SHC68-68-A2
         - NI
         - Test Cable Assembly
       * - SCB-68A
         - NI
         - Noise Rejecting Terminal Block
       * - SX6300
         - Colfax International
         - Colfax SC6300 Workstation
       * - 14UD-42X-24
         - TMC
         - Ultradamp Vibration Isolation with Casters
       * - 784-736-02R
         - TMC
         - 36x60x18\" Performance Series Optical Top Table

.. collapse:: Total Cost

    .. list-table::
       :header-rows: 1

       * - **Section**
         - **Cost (USD)**
       * - Illumination Path
         - \$42,419.67
       * - Detection Path
         - \$61,635.82
       * - Sample Positioning
         - \$18,869.78
       * - Shared Equipment
         - \$32,300
       * - **TOTAL**
         - **\$155,224.78**

---------------

Illumination Path
_________________

Our baseplate design was made with ease of assembly in mind. The basic process involves aligning Polaris posts with
dowel pins and screwing them using 1/4"-20 Screws in at the predetermined hole locations on the breadboard.
This general process is depicted below:

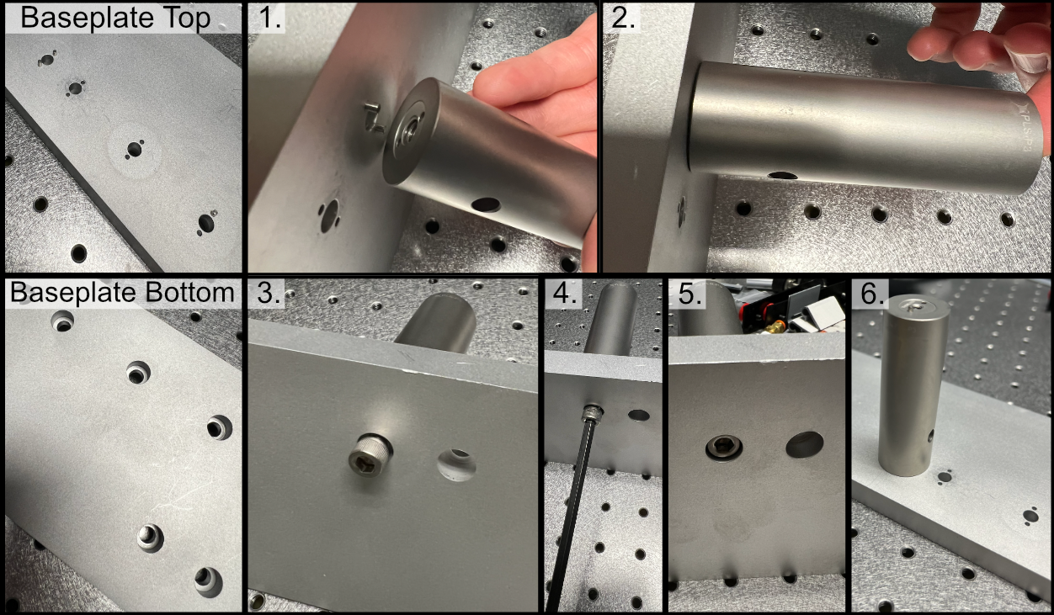
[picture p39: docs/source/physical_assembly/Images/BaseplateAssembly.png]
General process for baseplate assembly


    **Figure 1:** General process for baseplate assembly

To either mount the baseplate onto an optical table or onto separate posts, the process is similar in that
just requires screwing 1/4"-20 screws into either an optical breadboard or onto separate posts at the four corner
holes. For our system, we opted to mount our illumination baseplate on 1.5" tall `1" diameter Thorlabs pedestal posts
<https://www.thorlabs.com/newgrouppage9.cfm?objectgroup_id=851>`_. As a general note, having the illumination path
elevated instead of affixed directly into the table is both helpful to enable access to mounting and unmounting the
illumination optics as well as ensuring that the illumination objective and detection objective are able to be
aligned vertically with each other.

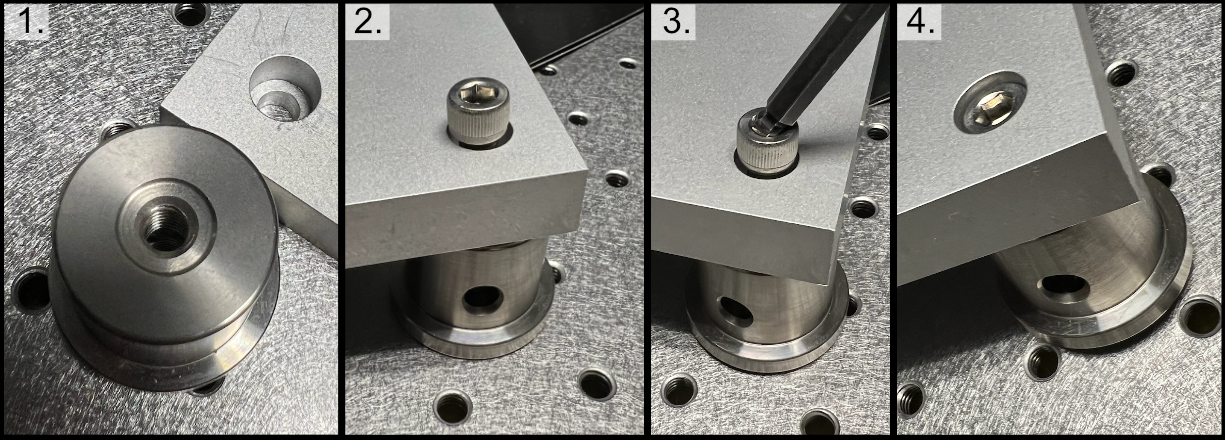
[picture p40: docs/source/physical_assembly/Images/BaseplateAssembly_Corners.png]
General process to place posts on baseplate corners


    **Figure 2:** General process to place posts on baseplate corners

---------------

Mounting Lenses
^^^^^^^^^^^^^^^

Mounting lenses into a Polaris lens mount and onto an associated post is a fairly straightforward process. The
general flow is shown in the image below, where first the flatter face of the desired lens should be placed such that
it is touching the metal boundary on the lens mount itself. Then the lens should be fixed into place by screwing the
lock screw on the top of the lens mount. With the lens secured in the mount, then two dowel pins should be placed in
the appropriate holes on the Polaris post, and then the lens mount should be placed such that the two holes on the
lens mount align with the pins on the Polaris post. Then the lens mount should be anchored into place by screwing it
into the Polaris post. Additional information can be found at `Thorlabs <https://www.thorlabs.com/newgrouppage9.cfm?objectgroup_id=10056>`_.

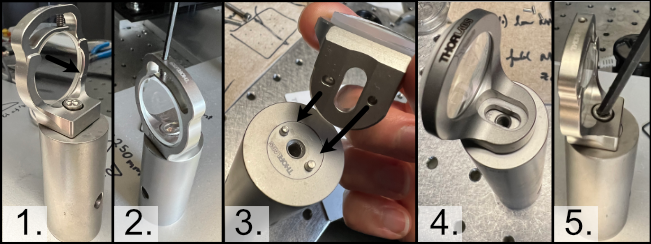
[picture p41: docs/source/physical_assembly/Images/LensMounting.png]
General process for mounting a lens into a Polaris holder and onto a post


    **Figure 3:** General process for mounting a lens into a Polaris holder and onto a post

---------------

Initial Laser Collimation and Alignment
^^^^^^^^^^^^^^^^^^^^^^^^^^^^^^^^^^^^^^^

When first assembling the system, ensuring proper output collimation from the fiber laser source is critical. There are multiple checks that one can take for this step, but we utilize a combination of a `shear-plate interferometer <https://www.thorlabs.com/newgrouppage9.cfm?objectgroup_id=2970>`_ and two pinhole apertures placed at opposite ends along the length of the baseplate. Shear-plate interferometers are designed to split and interfere an input beam of coherent light, such that when the beam is collimated there are interference fringes aligned vertically with a reference line. The fiber laser collimator we used for this system is the `Thorlabs CFC11A-A <https://www.thorlabs.com/thorproduct.cfm?partnumber=CFC11A-A>`_, which features an adjustable barrel which controls the position of collimation optics within the element.

The basic assembly process involves first inserting and fixing the CFC11A-A into a Thorlabs AD15S2 adapter, which allows it to then be mounted into a 2.5" Polaris K1XY mount. This assembly is then mounted onto the respective Polaris post at the start of the baseplate. The fiber laser source is then able to be directly mounted into the CFC11A-A, making sure that the protrusion on the fiber wire aligns with the open section of the CFC11A-A port. The basic process of ensuring collimation then involves turning on the laser source, and placing the shear-plate interferometer such that the input port aligns with the output of the laser unit. Then, by slowly adjusting the barrel of the CFC11A-A and observing the interference fringe orientations along the top display of the interferometer, one is able to adjust the beam until it is properly collimated.

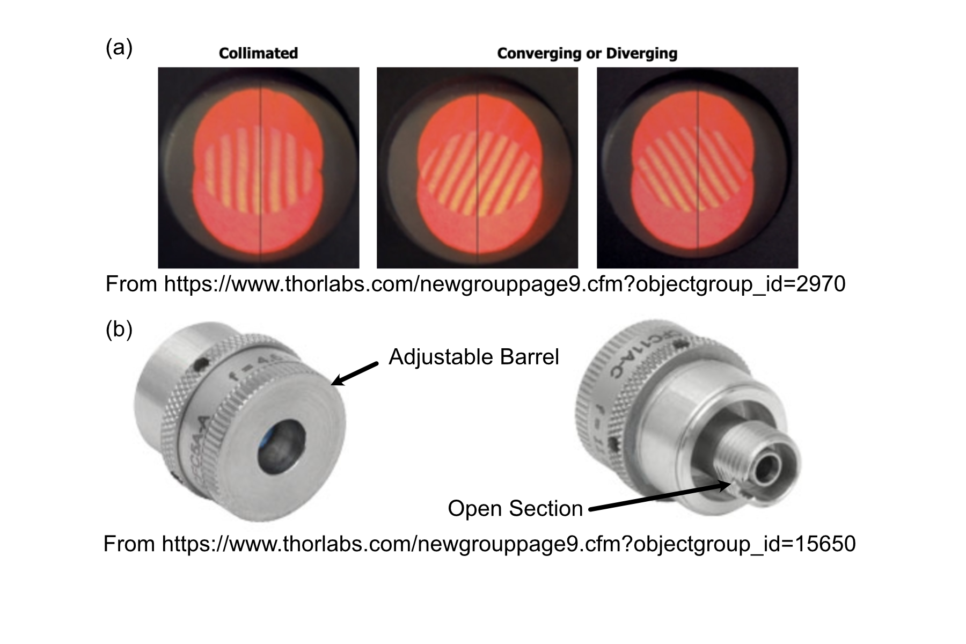
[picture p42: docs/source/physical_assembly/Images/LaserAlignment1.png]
Shear Plate interferometer and collimator lens


    **Figure 4:** Shear Plate interferometer and collimator lens

With the beam collimated, the process of beam alignment involves adjusting the position control knobs on the K1XY to have the beam pass through two pinhole apertures along the optical path. The height of the initial laser output is designed to be at 3.75" above the top surface of the baseplate, so selecting appropriate post heights for the apertures such that their centers rest at 3.75" is essential. In our case, we use `Thorlabs ID12 <https://www.thorlabs.com/thorproduct.cfm?partnumber=ID12>`_ pinhole apertures, so using a post height of 3.25" will ensure that they are at the proper height for alignment. We designed a `custom ID12 to Polaris adapter <https://github
.com/TheDeanLab/altair/tree/main/downloads/common/cad>`_ to ensure the aperture is at the proper height and properly aligned along the designated Polaris axis. When using this method, the ID12 to Polaris Adapters can just be directly mounted onto the holes designated for L1 and the Illumination Objective, depicted below, to cover the length of the baseplate. With the pinholes placed, the process becomes iterative by making small adjustments on the K1XY tip/tilt knobs and XY position screws until the beam passes through both pinholes.

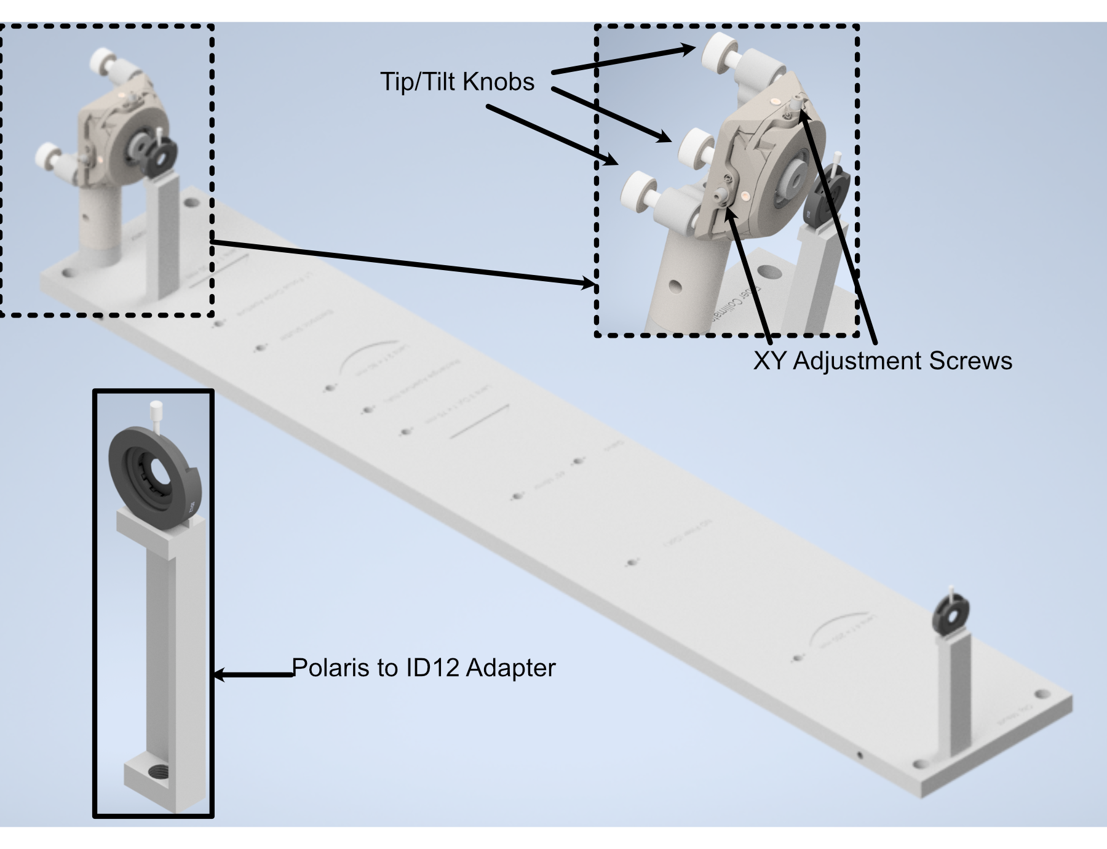
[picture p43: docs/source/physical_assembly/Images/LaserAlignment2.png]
Performing beam alignment across the baseplate


    **Figure 5:** Performing beam alignment across the baseplate

---------------

Mounting of Optic Posts
^^^^^^^^^^^^^^^^^^^^^^^

After ensuring basic collimation and alignment of the laser system, the next step is mounting the appropriate polaris
post size for each optical element in the system. The overall breakdown of which size posts went with each hole
location is listed below. Where holes (3), (4), and (10) are placements for optional elements in the system. (3) is
meant for the placement of an adjustable pinhole aperture, where the same ID12 to Polaris Adapter system used in
the alignment step can be placed. Otherwise a 0.5" post holder can be placed here, and then the ID12 or ones pinhole
aperture of choice can be mounted on a 0.5" post. (4) is dedicated placement for an electronic shutter in the event
that the laser being used for the system isn't directly controlled via a computer, and helps to ensure that laser
light is not photobleaching a sample unless imaging is taking place. (10) is dedicated space for a neutral density
(ND) filter, in the event that the power of the laser used needs additional reduction not directly addressable
through the laser controls itself.

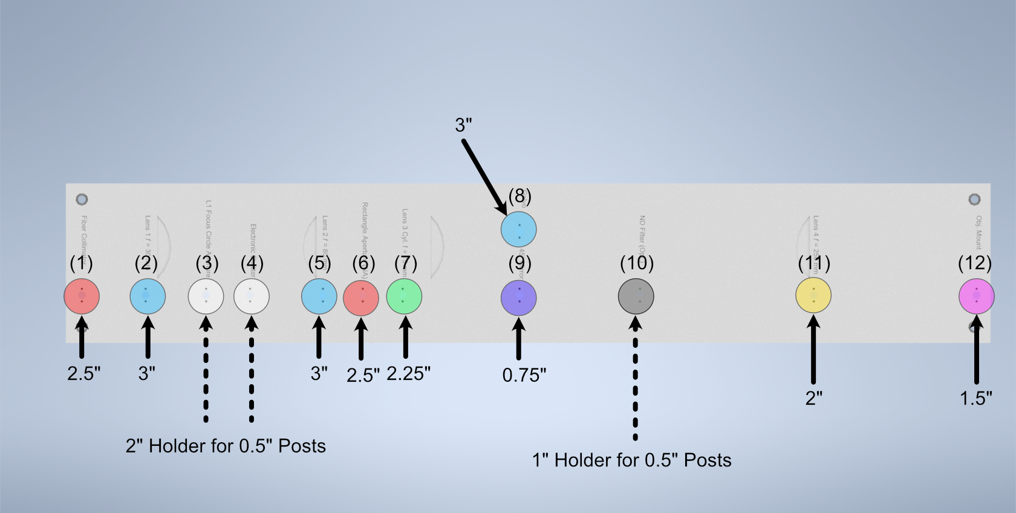
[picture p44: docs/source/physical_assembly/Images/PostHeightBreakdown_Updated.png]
Schematic of which holes use which post heights


    **Figure 6:** Schematic of which holes use which post heights

---------------

Mounting of Optics
^^^^^^^^^^^^^^^^^^

With the posts in place, the next step involves mounting the optics elements themselves onto the posts. When mounting elements (6), the VA100 rectangular aperture, and (7), the RSP1 rotation mount, it should be noted that the corresponding element should first be fixed onto their respective Polaris adapter and then onto the Polaris posts. In addition, take measures to mount the 45 degree mirror (9) fully prior to mounting the resonant galvo to ensure that the galvo is not accidentally hit during installation of the 45 degree mirror.

To construct the 45 degree mirror assembly, first mount the Polaris K1S4 onto the Polaris-MA45 45 degree mounting adapter, and then place a 1" diameter mirror into the K1S4 and secure it using the K1S4 mounting screw.

To construct the illumination objective assembly, first mount the Polaris 1XY onto its respective 1.5" post. The threading of the 1XY (SM1) does not match that of our illumination objective used (M25x0.75), so an SM1A12 adapter must first be installed onto either the 1XY or the illumination objective. Then, the objective can be mounted onto
the 1XY.

---------------

Final Alignment Adjustments
^^^^^^^^^^^^^^^^^^^^^^^^^^^

Once all the optics have been properly mounted, the final step for ensuring a working illumination path is to center
the beam after the 45 degree mirror onto the center of back lens surface of the illumination objective. The primary
method of doing this is through adjusting the xy tip/tilt knobs on the K1S4 Polaris mount that houses the 45 degree
mirror.

---------------

Detection Path
______________

Detection Path Assembly
^^^^^^^^^^^^^^^^^^^^^^^

Our detection path consists of our Nikon N25X-APO-MP detection objective, Hamamatsu ORCA Flash4.0 V3 Camera, ASI
C60-TUBE-400 tube lens, and ASI FW-0002-8 8-position filter wheel unit. These components are mounted together and
affixed onto an ASI LS-100-AMCCH translation stage for focus control. We currently use a prototype detection path
baseplate (available here) as a mounting stage for these elements and the sample chamber; however, this additional
baseplate is still undergoing design iterations and is not critical for a functional detection path.

We utilize two additional custom adapter elements in the construction of the detection path: a shell casing around
the tube lens that mounts to the translation stage and an adapter for the translation stage to mount it to an optical
breadboard table. The height thicknesses of these elements were chosen such that the height of the detection
objective center should match that of the illumination objective (which with the 1.5" tall posts our illumination
baseplate rests on is 4.75" above the optical table surface). These elements can be custom machined if desired;
however, we have found 3D printed PLA variants to perform their functions effectively as well.

The assembly of the detection path begins with the translation stage and it's associated breadboard adapter
(available here in two variants, based on whether or not one is using the 0.5" thick detection path baseplate):

    1. Turn the translation stage upside-down
    2. Place the breadboard adapter upside-down on top of the inverted translation stage (such that the raised
       platform of the adapter is touching the bottom side of the translation stage)
    3. Align the recesses on the bottom of the adapter with the holes on the bottom of the translation stage
    4. Fix the adapter onto the translation stage by screwing M6 screws into the recesses aligned with the
       translation stage holes.

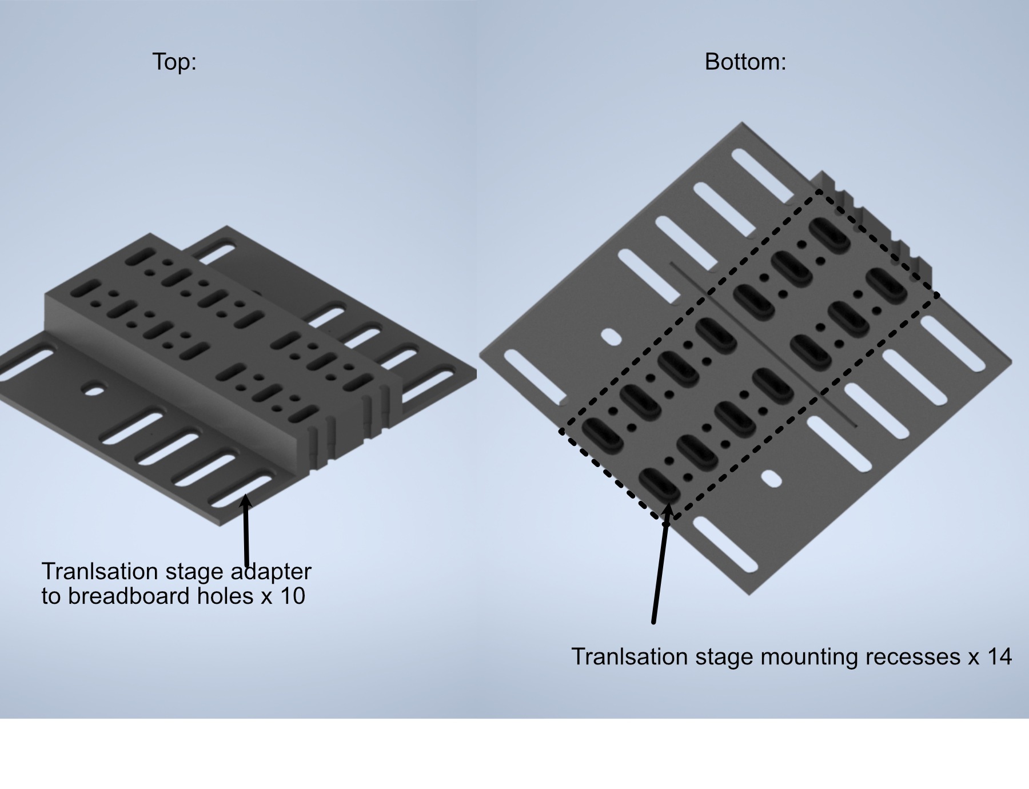
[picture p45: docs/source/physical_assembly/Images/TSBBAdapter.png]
Schematic of the translation stage breadboard adapter


    **Figure 7:** Schematic of the translation stage breadboard adapter

The next step is flipping the translation stage assembly right side up again, and then fixing the first of two halves
of the tube lens adapter onto the top of the translation stage:

    1. Place the tube lens adapter half onto the top of the translation stage such that the block with two sets of
       five recessed holes is touching the top of the translation stage.
    2. Align the Recess holes on the adapter with the holes on the top of the translation stage.
    3. Fix the adapter onto the translation stage by screwing M6 screws into the aligned recess holes

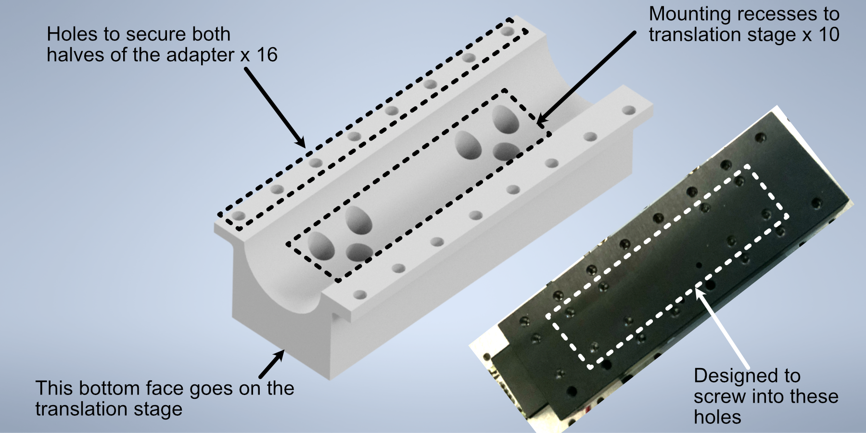
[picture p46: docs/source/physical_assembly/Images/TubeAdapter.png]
Schematic of the tube lens to translation stage adapter


    **Figure 8:** Schematic of the tube lens to translation stage adapter

Next, we'll focus on assembling the tube lens and filter wheel:

    1. Take the MIM to Filter wheel adapter and fix it onto the front port of the filter wheel using the associated
       screw ports
    2. With the adapter fixed, now screw the 400 mm tube lens into the adapter.

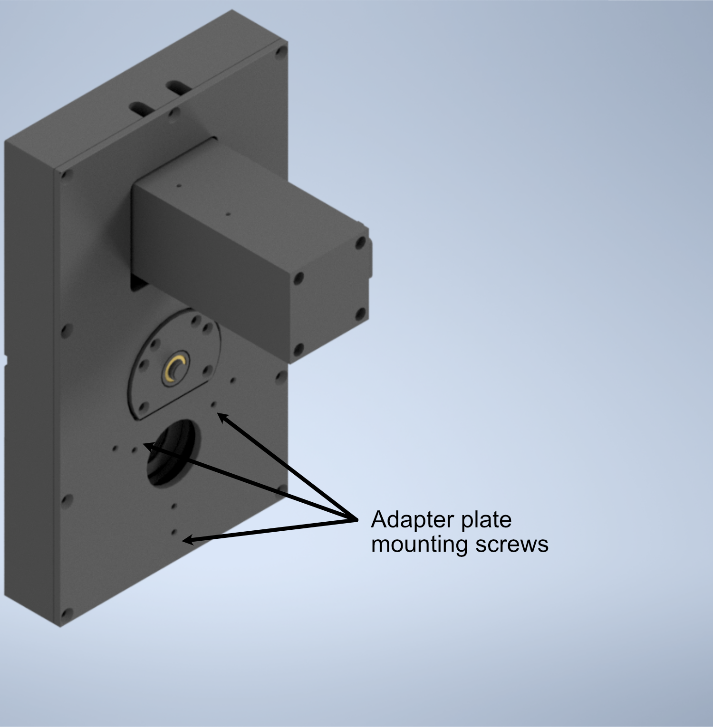
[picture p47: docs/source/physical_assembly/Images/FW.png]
Schematic of the filter wheel port for the tube lens


    **Figure 9:** Schematic of the filter wheel port for the tube lens

In order to fix our detection objective onto the tube lens, we must first prepare an extension and threading adapter:
    1. Take the C60-EXT-15 15 mm Tube extension piece and place the RAO-0051 M32x0.75 threaded sleeve inside
    2. Using the screws on the top of the extension piece, fix the threaded sleeve in place
    3. Insert/screw the extension piece into the front of the tube lens.

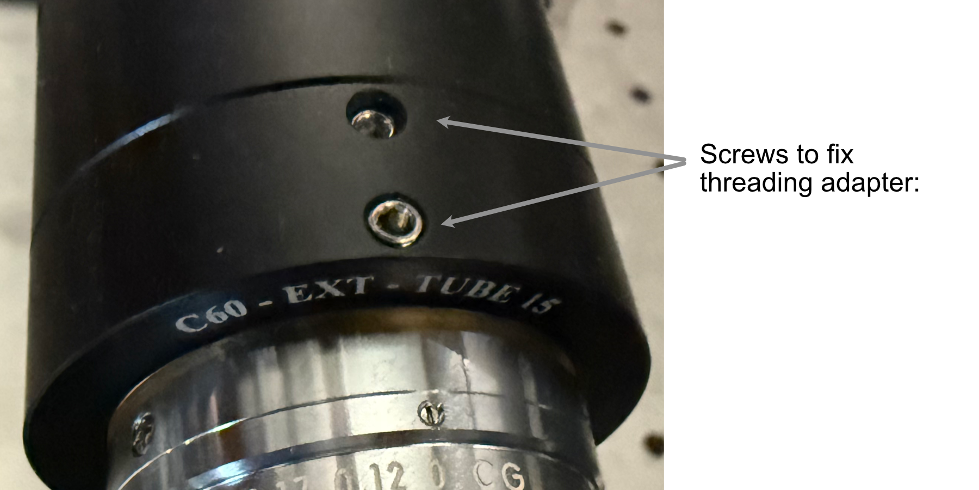
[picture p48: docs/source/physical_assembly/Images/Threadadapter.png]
Showcase of the screws used to secure the thread adapter for the tube lens


    **Figure 10:** Showcase of the screws used to secure the thread adapter for the tube lens

The tube lens assembly is now ready to be fixed onto the translation stage assembly:
    1. Place the tube lens assembly such that the tube lens lies within the curved region of the tube lens adapter
    2. While there isn't an exact science to the relative placement of the tube within the adapter, try to position
       it such that more of the tube is extended out on the side where the objective will be mounted (our setup is shown
       below for reference).
    3. Place the second half of the tube lens adapter such that the curved side fits onto the lube lens and position
       it such that the holes of both halves of the adapter align with each other.
    4. Using your choice of either M6 or 1/4"-20 screws and associated washers/nuts, place the screws with a washer
       placed on them first into the aligned holes of the adapter. We used 4 of the adapter holes on each side, but
       more can be used for extra security if desired.
    5. Screw a washer onto each of the screws until they're secured against the bottom lip of the adapter.

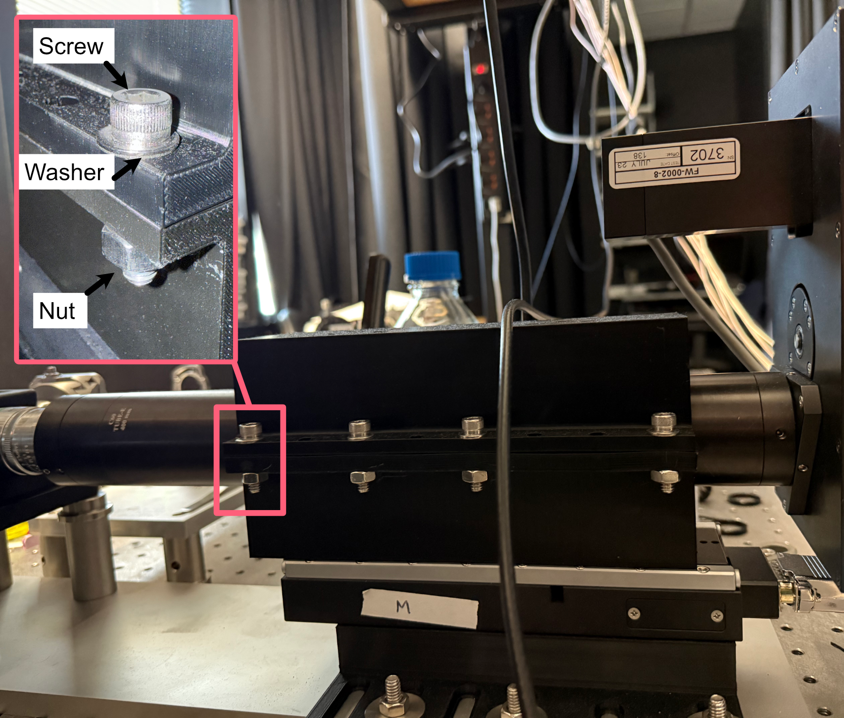
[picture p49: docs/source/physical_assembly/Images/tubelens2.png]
Example of tube lens mounted in the corresponding adapter


    **Figure 11:** Example of tube lens mounted in the corresponding adapter

The detection path assembly can now be fixed into place onto either the detection path baseplate or the optical
table, keep in mind this process is meant to essentially place the unit in the ballpark of where it should be, finer
adjustments will be made afterwards:

    1. Using the mounting holes on the translation stage assembly, place the assembly such that the edge of the
       translation stage adapter facing the illumination path is roughly 9-10" away from the location of the
       illumination objective.
    2. Using the adjacent edge of the translation stage adapter (the one that should be perpendicular to the
       orientation of the illumination path), try to align the side of the adapter with the mounting hole of the
       illumination objective.
    3. Screw the translation stage adapter into either the optical table to the detection path baseplate (we
       recommend using `Thorlabs 1" Spacers <https://www.thorlabs.com/newgrouppage9.cfm?objectgroup_id=851>`_ in place
       of washers here).

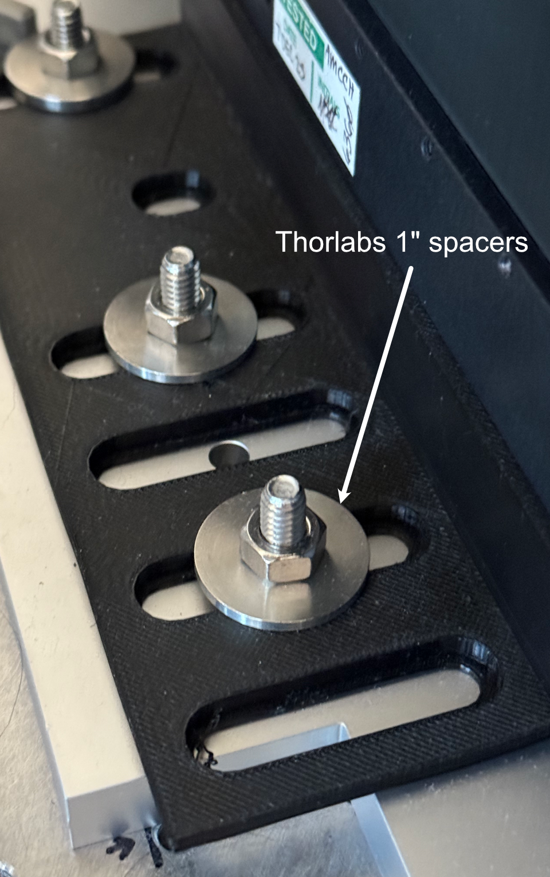
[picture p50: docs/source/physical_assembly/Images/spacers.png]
Example of our setup for securing the translation stage to breadboard adapter onto our detection path

          baseplate
    :width: 300px

    **Figure 12:** Setup for securing the translation stage to breadboard adapter onto our detection path baseplate

With the assembly fixed in place, the camera can then be screwed into the filter wheel:
    1. Align the front thread of the camera with the back port of the filter wheel
    2. Screw the camera into the filter wheel until there is resistance
    3. Slowly adjust the camera tilt until the top surface is leveled (we use a bubble leveling tool for this, shown
       below)

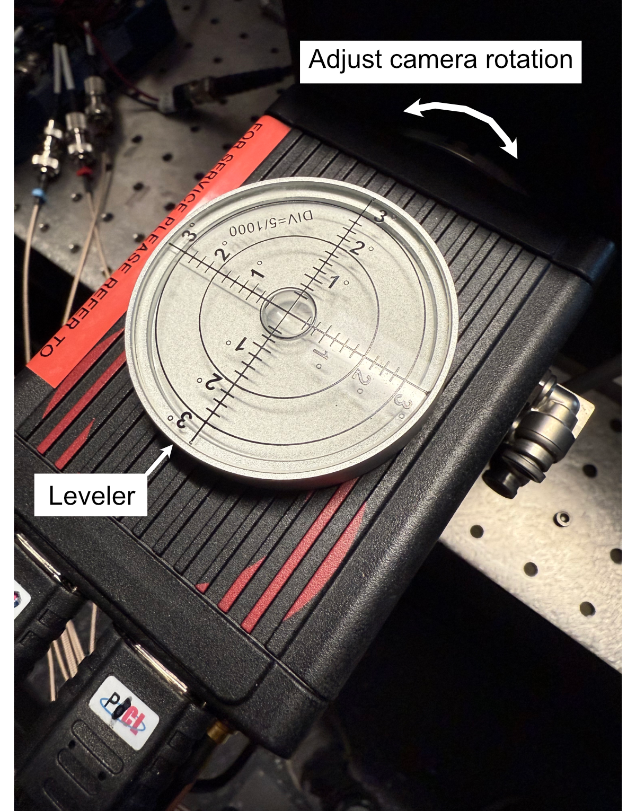
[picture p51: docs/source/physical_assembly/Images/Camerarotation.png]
Mounting of the camera


    **Figure 13:** Mounting of the camera

The final steps to to assemble the detection path are to screw the detection objective into the front of the tube
lens and attach all associated wires to the camera, filter wheel, and translation stage. If there's not enough
clearance between the front of the tube lens and the sample chamber to screw in the detection objective, the
translation stage might need to be wired up first and translated backwards manually using either navigate or the
Tiger Control Panel software.

---------------

Detection Path Positioning
^^^^^^^^^^^^^^^^^^^^^^^^^^

To position the detection path correctly, there's two primary steps: Initially ensuring the detection objective slides into the correct port on the fixed sample chamber and then ensuring that the light sheet is centered in the FoV of the camera, typically done by putting  fluorescein into the water-filled chamber.

**Step 1: Ensuring the detection objective slides into the sample chamber port**
    1. It's recommended to start with your detection path translation stage set far enough back such that there is anywhere from 0.5-1" or more of space between the front of the detection objective and the sample chamber.
    2. Within navigate or the Tiger Controller software, start to slowly move the objective forward (initially increments of 1000 um should be okay, but as the objective approaches the port the distance should be significantly lowered to 100 um or below to ensure the objective isn't damaged).
    3. If the objective isn't centered properly, the screws/nuts on the translation stage to breadboard adapter (see figure 12) can be loosened slightly and the detection path assembly can be carefully positioned horizontally, taking care that the unit isn't tilted at an angle going into the objective port, and then re-tightened.

Once the detection objective properly translates into it's port, the tilt alignment can be further refined by slowly translating the detection objective forward towards the illumination objective, taking great care that they don't touch each other. If there is a significant tilt in the detection path compared to the illumination path, it should be fairly evident in the diagonal space between the objectives (ideally it should look roughly equal in width between the two objectives). As example of the relative position of our objectives when the detection objective is properly placed at the focus of the illumination objective is shown below to give a visual reference for users.

Once the position of the detection objective is acceptable, further refinement of it's position can be done by first filling the chamber with water and then adding roughly ~100 microliters of f fluorescein into the chamber. Fluorescein  is useful as a visualization tool to be able to see the beam coming out of the illumination objective with the naked eye. With fluorescein in the chamber, the position of the detection objective can be translated to align with the focus of the beam itself (shown below)

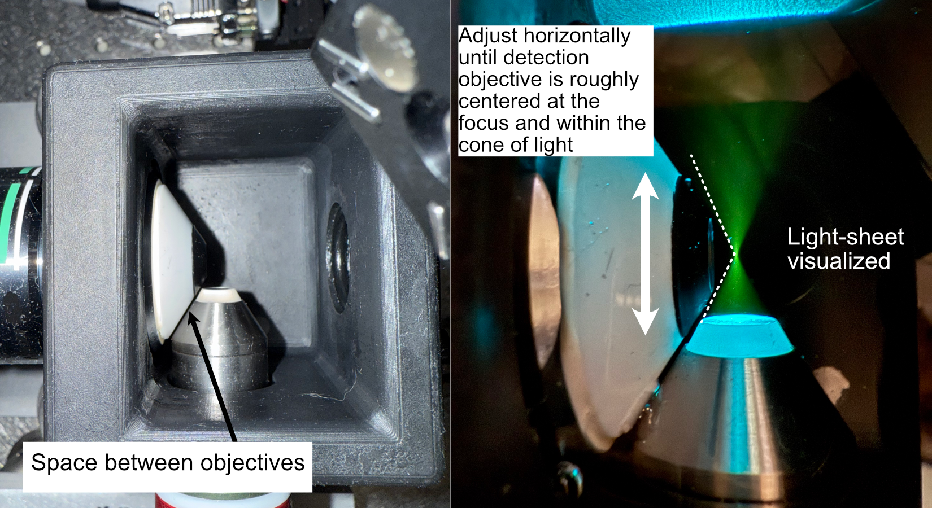
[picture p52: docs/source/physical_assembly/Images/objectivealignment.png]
Physical alignment of the detection objective


    **Figure 14:** Physical alignment of the detection objective

**Step 2: Focus refinement**
    With the detection objective roughly in the correct location, further refinement is done by turning on the camera and imaging the fluorescein light-sheet to find the focus by adjusting the focus translation stage in small increments (50 microns for large movements, 1-5 microns for small movements). The goals during this step are to ensure that the detection objective focus is at the focus of the illumination objective, to make sure the light-sheet focus is centered on the image FoV from the camera, and that the light-sheet is aligned vertically in the image FoV.

    Finding the focus is often something that just comes with experience of using the system itself; however, here are some general methods to follow that can help get one's bearings:
        1. In general, as the detection objective approaches the light sheet focus, an envelope of light should start to appear (see below), ideally this envelope will be horizontal across the FoV. If it horizontal or has some tilt to it, adjusting the tip/tilt of the 45 degree mirror and the rotation of the cylindrical lens. In addition, ideally this envelope will be centered vertically in the FoV, which can be set by adjusting the y adjustment screw on the illumination objective mount.
        2. Towards the focus location, a dark vertical region with horizontal striations should appear. Once this region is visible, using small translation distances (~1 um or finer) to find the position that makes both the vertical region and horizontal striations look as sharp as possible should be done.
        3. If the dark region isn't centered on the image FoV, adjusting the x and y adjustment screws on the illumination objective mount and making slight horizontal translations on the detection path can help.
        4. In general doing these adjustments in small increments is helpful, as once adjustments to the various elements may require readjusting the focus translation stage position to keep track of the focus.

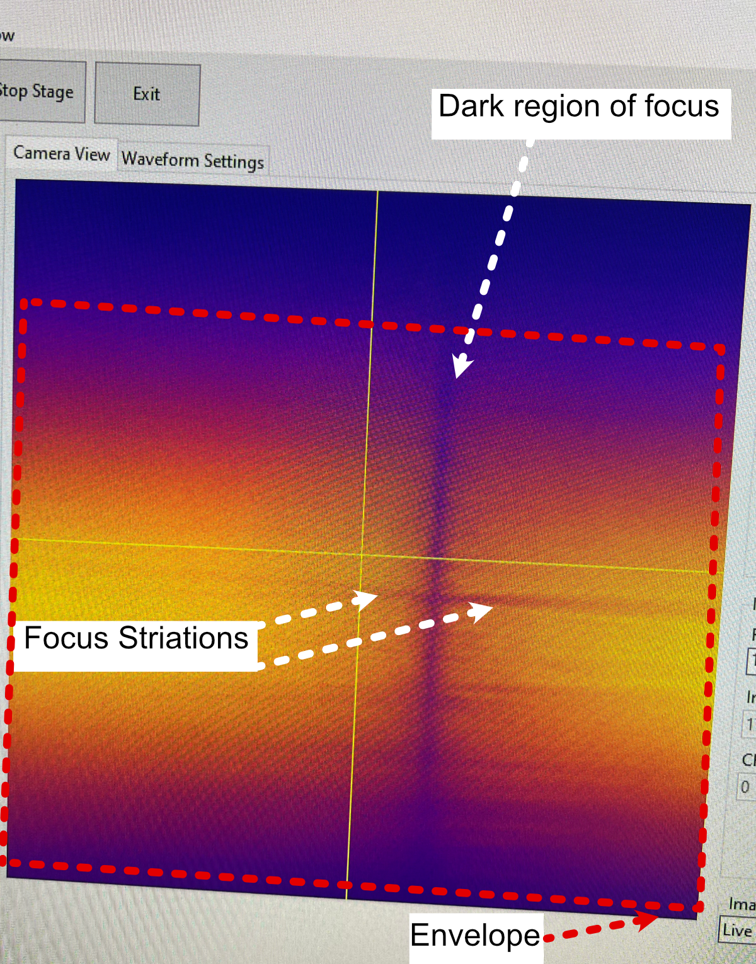
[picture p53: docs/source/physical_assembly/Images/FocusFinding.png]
Breakdown of the light sheet focus within navigate


    **Figure 15:** Breakdown of the light sheet focus within navigate

---------------

Optomechanics
_____________

Visualization of Axes Mapping
^^^^^^^^^^^^^^^^^^^^^^^^^^^^^

In our system we have 5 different translation stages at work: the standard x,y, and z axes, an additional stage along the z axis to control the focus of the detection path (f), and and axis associated with the piezo positioned such that its normal is 60.5 degrees away from the y-axis.

Layout of how the axis of the system are mapped

    **Figure 16:** Layout of how the axis of the system are mapped

.. note:: **Coordinate System Differences**

   The coordinate axes used in **optical simulations** differ from those in the **physical microscope system**
   controlled by **navigate**. This discrepancy arises from **standardized axis conventions** in Zemax versus
   those historically used in our previous systems. Users should be mindful of this distinction when interpreting
   simulation results versus real-world microscope operation. The differences are illustrated below:

   Difference in coordinate axes for simulation and physical setup

---------------

The Piezo Angle Mount
^^^^^^^^^^^^^^^^^^^^^

We designed a custom angled mount for our `Piezoconcept HS1 piezo <https://piezoconcept-store.squarespace
.com/1-axis/p/hs1>`_ in order to be able to scan our sample easily between our two objectives by translating a single motorized unit (in this case the piezo), instead of having to calculate and program the movement of two translation stages in tandem for both the y and z directions. The anatomy of our angled mount is broken down in the figure below, where there are four translation stage mounting holes to attach the unit to an ASI translation stage, nine Piezo mounting holes that correspond to the mounting scheme of our piezo unit, as well as four through-holes and a window for ease of access for the mounting process. We provide the CAD files for this mount `here <https://github
.com/TheDeanLab/altair/tree/main/downloads/common/cad>`_, and have had success in using both 3D printed and aluminum machined versions of the unit. It's recommended to first mount the angle mount onto the translation stage unit before mounting the piezo on the angle mount to ensure access to all the through-holes.

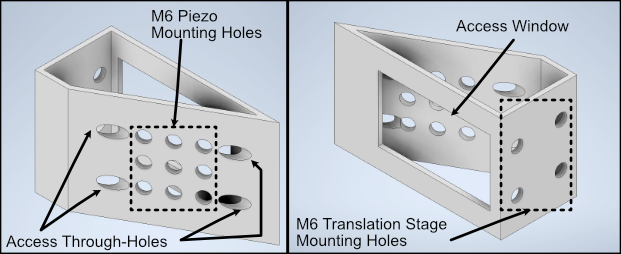
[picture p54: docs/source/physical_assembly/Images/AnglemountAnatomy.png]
Breakdown of our custom angle piezo angle mount


    **Figure 17:** Breakdown of our custom angle piezo angle mount.

The installation of our custom angled piezo mount is designed to be directly compatible with ASI translation stages. ASI translation stages feature M6 hole pairs that are spaced along the length of the translation stage at intervals dependent on the specific stage one is using. The mounting process involves aligning these 4 holes with 4 of the M6 holes on the translation stage and screwing them in. For ease of screwing in the base, there are four through holes on the angled face of the mount shown in B that a screwdriver is able to pass directly through to screw as shown in C. An alternative method of mounting is shown in D, where the window on the back of the angle mount is able to be screwed through as well.

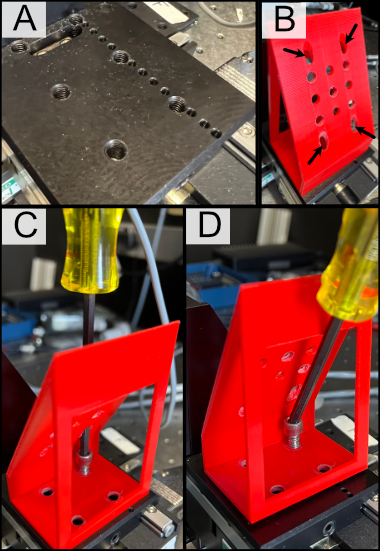
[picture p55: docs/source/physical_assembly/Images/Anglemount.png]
General process for mounting our piezo angle mount onto an ASI translation stage


    **Figure 18:** General process for mounting our piezo angle mount onto an ASI translation stage

---------------

Sample Holder Design
^^^^^^^^^^^^^^^^^^^^

Our sample holder design is built for imaging cells on a `5 mm coverslip <https://www.fishersci.com/shop/products/5mm-cover-slip-german-glass/50949439>`_, and is shown below. The design features a clamp-like method of securing the 5 mm coverslip in place, where the coverslip rests in an inset region and the clamp is screwed in via an M1.6 screw in the back of the holder. All associated files for this design and other custom parts can be found `here <https://github.com/TheDeanLab/altair/tree/main/downloads/common/cad>`_.

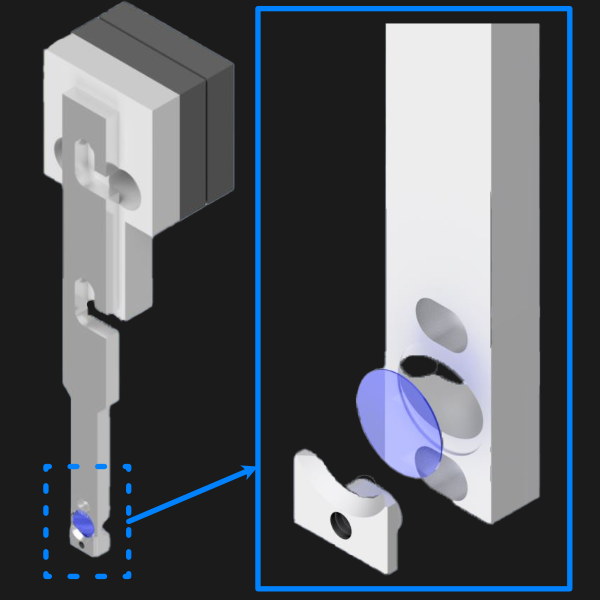
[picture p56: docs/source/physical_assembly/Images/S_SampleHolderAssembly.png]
5 mm coverslip sample holder design


    **Figure 19:** 5 mm coverslip sample holder design.

---------------

Assembling the Magnetic Sample Mount
^^^^^^^^^^^^^^^^^^^^^^^^^^^^^^^^^^^^

As a safeguard for the risk of the sample crashing into either the illumination or detection objective during sample positioning or imaging, we opted to incorporate a magnetic mount for our sample holder. We use a Thorlabs KBT1X1T and KBB1X1 as our magnetic mount pair, and then mount our sample holder onto the KBT1X1T using a  `custom adapter <https://github.com/TheDeanLab/altair/tree/main/downloads/common/cad>`_. The KBB1X1 is affixed to the piezo using an M2.5 screw, and using a small leveling tool (shown below) during this step is helpful to ensure that the magnetic base is mounted as level as possible for the imaging process.

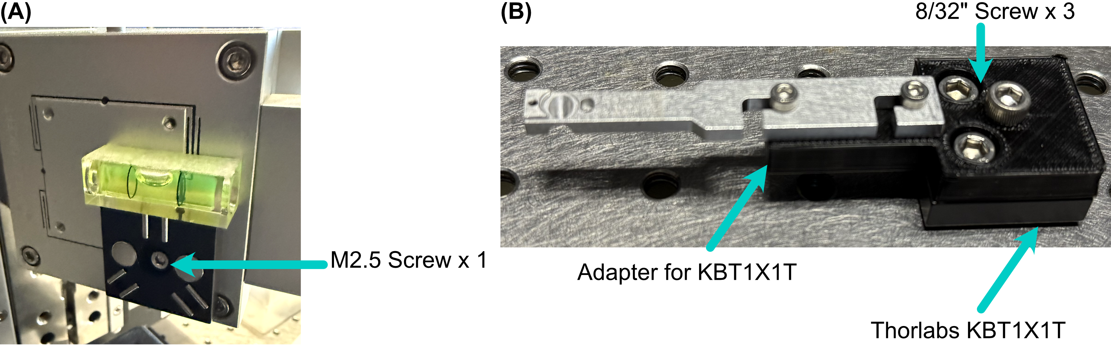
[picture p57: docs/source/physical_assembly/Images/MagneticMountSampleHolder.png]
Basic assembly of magnetic sample holder mount


    **Figure 20:** Basic assembly of magnetic sample holder mount

---------------

Optoelectronics
_______________

Wiring Diagram
^^^^^^^^^^^^^^

Our complete microscope assembly features a variety of different optoelectrical and optomechanical elements. These
elements are primary controlled via our NI DAQ (PXIe-6738) or our ASI Tiger Controller (TG16-BASIC), which are then
controlled via navigate during the imaging process. The diagram below depicts how these elements are wired together,
as well as an individual pinout designation table for the pin configurations we used on our DAQ.

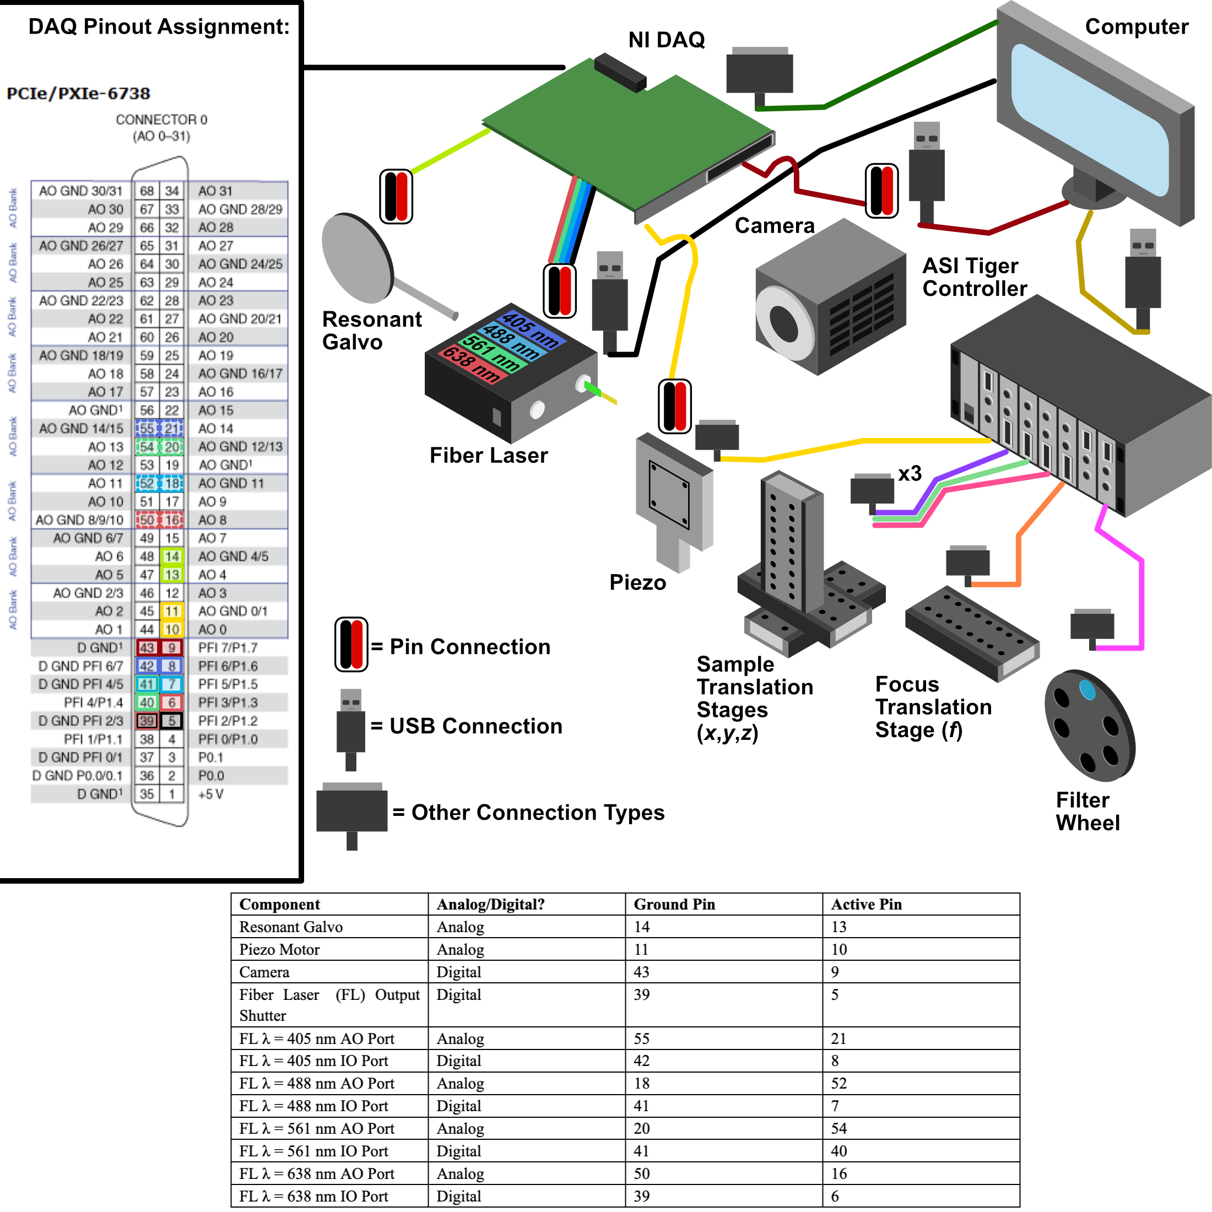
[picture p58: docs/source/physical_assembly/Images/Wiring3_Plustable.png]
Wiring diagram for the Tiger Controller, DAQ, and associated elements.


    **Figure 21:** Wiring diagram for the Tiger Controller, DAQ, and associated elements.

---------------

Piezo Setup & Troubleshooting
^^^^^^^^^^^^^^^^^^^^^^^^^^^^^

On the PCI Board, connect the positive and negative wires  to the corresponding analog output (AO) you want, in our case
we used AO 0, so we connected the positive wire to pin 10 and the ground to pin 11, then plug the BNC cable connected to
those wires into the EXT IN input on the Tiger controller panel corresponding to the piezo.

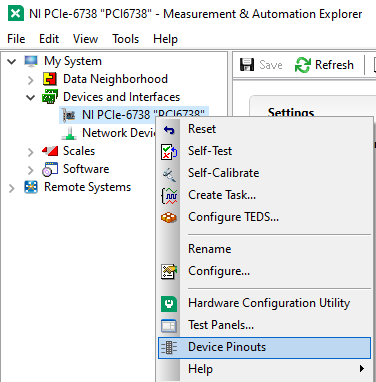
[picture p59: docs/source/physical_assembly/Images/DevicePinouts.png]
How to find the Device Pinout panel


    **Figure 22:** How to find the Device Pinout panel in NI MAXX.

Plug the piezo cable into the PIEZO input on the Tiger controller panel corresponding to the piezo, and verify the range of the piezo in the Tiger Controller software:

.. code-block:: none
   :caption: Verifying Piezo Range in Tiger Controller Software

   # Verify the range of the piezo in the Tiger controller software
   5 cca x?

   # Example output:
   :A  Q:P1
   23 P 1 100um RANGE
   24 P 2 200um RANGE
   35 P S 150um RANGE
   36 P 3 300um RANGE
   37 P 5 500um RANGE
   34 P f 50um RANGE
   25 P 4 350um RANGE:N-4

This tells us that our Piezo (Panel 5/Q) corresponded to P1 or a 100 um range, but ASI requires the piezo needed to be
set to  a 50 um range to be able to be initialized instead. To change this, we used the command ``5 cca x = 34`` and
power cycled the controller. Once the controller was powered back on, we verified the range again with the ``5 cca x?``

.. code-block:: none
   :caption: Verifying Piezo Range in Tiger Controller Software

   # Verify the range of the piezo in the Tiger controller software
   5 cca x?

   # Example output:
   :A  Q:Pf
   ...

Now we can see that the piezo is set to the correct range (Pf). With that verified, now confirm that the voltage output from the PCI Board is working:

| 1. Put the BNC cable input currently in EXT IN on the Tiger control panel into the input of the oscilloscope instead.
| 2. Go to the test panels for the PCI board in NI MAX.

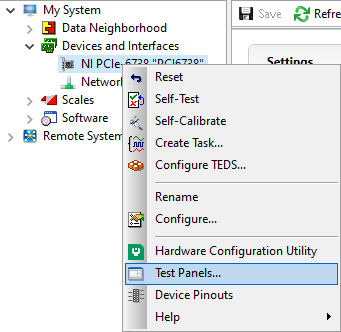
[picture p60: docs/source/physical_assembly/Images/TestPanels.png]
How to find the Test Panels panel


    **Figure 23:** How to find the Test Panels panel in NI MAXX.

| 3. Set the voltage mode to sinewave generation.
| 4. Set the voltage range to be between 0 to 10 V.
| 5. Set the frequency to a desired value (we ended up setting it pretty high at 10000 Hz for ease of viewing on the oscilloscope).

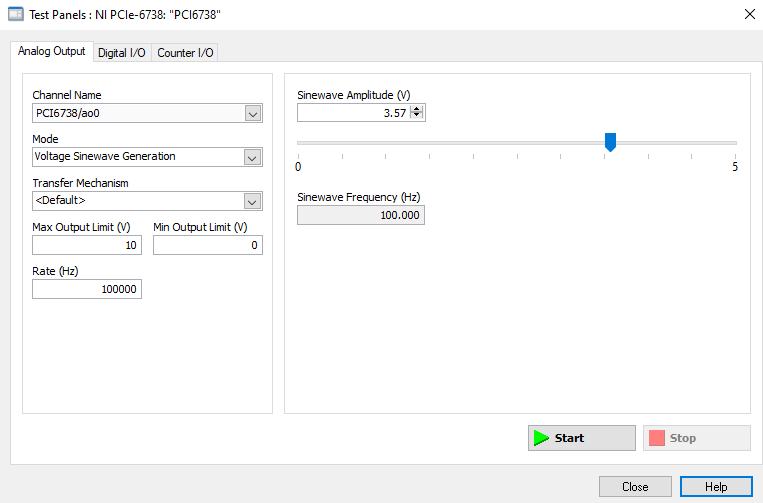
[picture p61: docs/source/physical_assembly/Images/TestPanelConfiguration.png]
How to find the Test Panels panel.


    **Figure 24:** How to generate analog output voltages with NI MAXX for testing purposes.

With the voltage output of the PCI board verified, plug the PCI Board voltage cable output back into the EXT IN slot and
verify that the position output of the Piezo reads similarly on the oscilloscope:

    1. Plug a BNC Cable into the SENSOR OUT connection on the tiger controller panel.
    2. Plug the other end of that cable into the oscilloscope.
    3. Verify that a sinewave output is seen on the oscilloscope.

If the PCI Board voltage is working as intended but the piezo position output doesn't seem to work, try ensuring that
the piezo is set in `External Input mode, and not Controller Input mode <https://asiimaging.com/docs/commands/pm>`_:

    1. Use the ``PM Q?`` (Our piezo corresponds to Q) command:
        - the output was ``Q = 0`` originally, telling us that it's in Controller Input mode
    2. Use the ``PM Q = 1`` command to set the piezo into External Input mode:
        - now the output of ``PM Q?`` is ``Q = 1``

Another important step is to ensure that the configuration file associated with navigate is appropriately set up for your piezo. This involves setting the correct axis and voltage-to-distance mapping for the piezo. As an example our configuration file for navigate looks like the following for setting up our piezo:

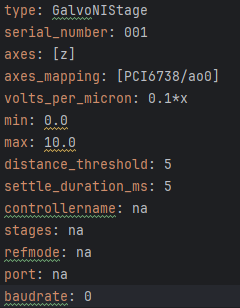
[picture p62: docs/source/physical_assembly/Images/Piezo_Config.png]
Navigate configuration file for the piezo.


    **Figure 25:** Navigate configuration file for the piezo.

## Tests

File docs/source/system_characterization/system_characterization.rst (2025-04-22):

.. _characterization-home:

###############################
System Characterization
###############################

Beam Characterization and PSF Analysis
________________________________________

To characterize our constructed system, we first image the generated light-sheet using the sample chamber transmission configuration shown below, where the illumination objective is placed directly in front of the detection objective. The image of our light sheet is shown in (a) below, where the cross-sectional profile of the light-sheet is shown in (b) and reveals a z-FWHM of ~0.415 um.

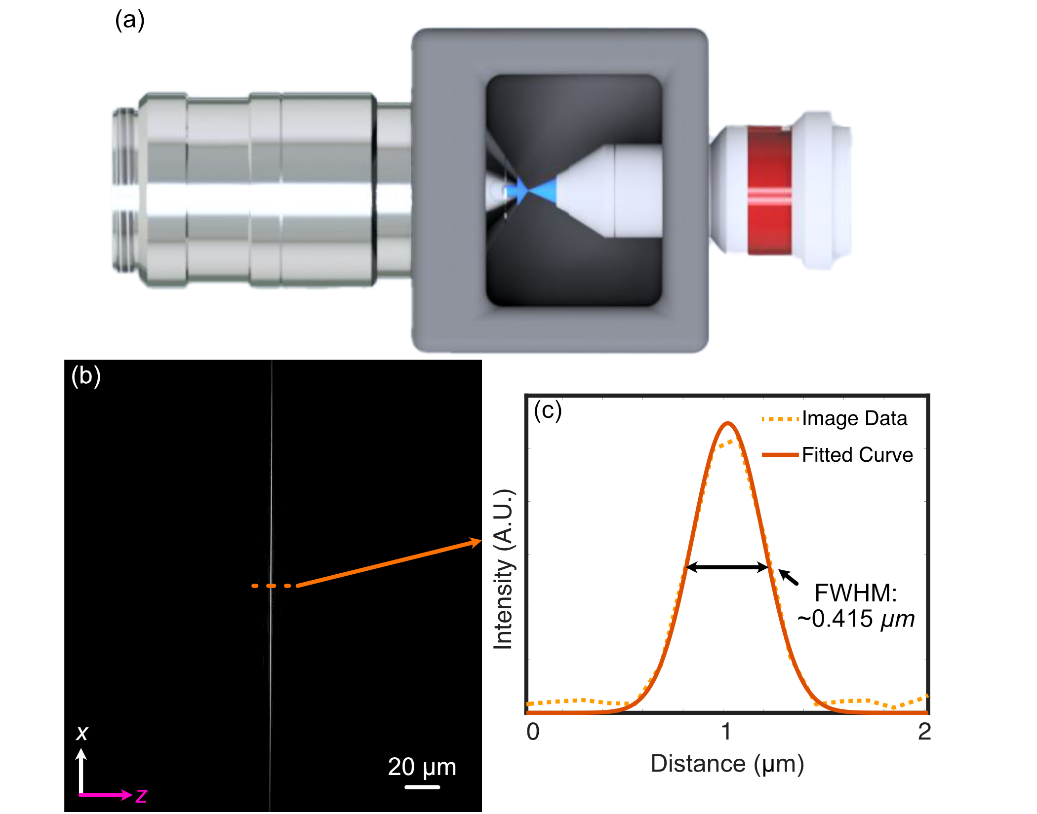
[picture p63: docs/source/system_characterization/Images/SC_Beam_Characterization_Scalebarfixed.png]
Analysis of the experimental lightsheet characteristics


    **Figure 1:** Analysis of the experimental lightsheet characteristics

To characterize the resolution of our system, we utilize 100 nm YG Fluorescent Beads (ID: 17150-10) from Polysciences Inc. The beads are first affixed onto a 5 mm coverslip using the following protocol:

.. note:: **Affixation protocol for 100 nm beads**

    1. Assemble petri dish, coverslip, and 5mM concentration (3-Aminopropyl)triethoxysilane (APTS)
    2. Put 5 mm coverslip in petri dish
    3. Apply ~100 microliters of (3-Aminopropyl)triethoxysilane (APTS) on top of coverslip
    4. Allow APTS to incubate for ~10-30 minutes
    5. Wash coverslip lightly with DI water 3 times
    6. Put beads of desired dilution (typically 10^-3 or 10^-4 for a normal distribution, 10^-6 for a sparse
       distribution) onto coverslip and allow to incubate between 2-20 minutes. Longer incubation time allows for more
       beads to adhere to the coverslip
    7. Wash lightly afterwards with DI water

After affixation, the beads are then imaged, the results of which are shown below. The PSF of an isolated bead is shown below in (a-c), where each image is a different orthogonal perspective of the bead's intensity distribution, and provide us insight into the resolution of our system in each orthogonal direction. We then provide Gaussian-fitted distributions of the FWHM of the population of fluorescent beads across a given z-stack in (d), both before and after applying deconvolution procedures. Prior to deconvolution, the average FWHM values across the bead population were 328 in x, 330 nm in y, and 464 nm in z. After deconvolution with PetaKit5D, these values improved to 235.5 nm in x, 233.5 nm in your, and 350.4 in z.

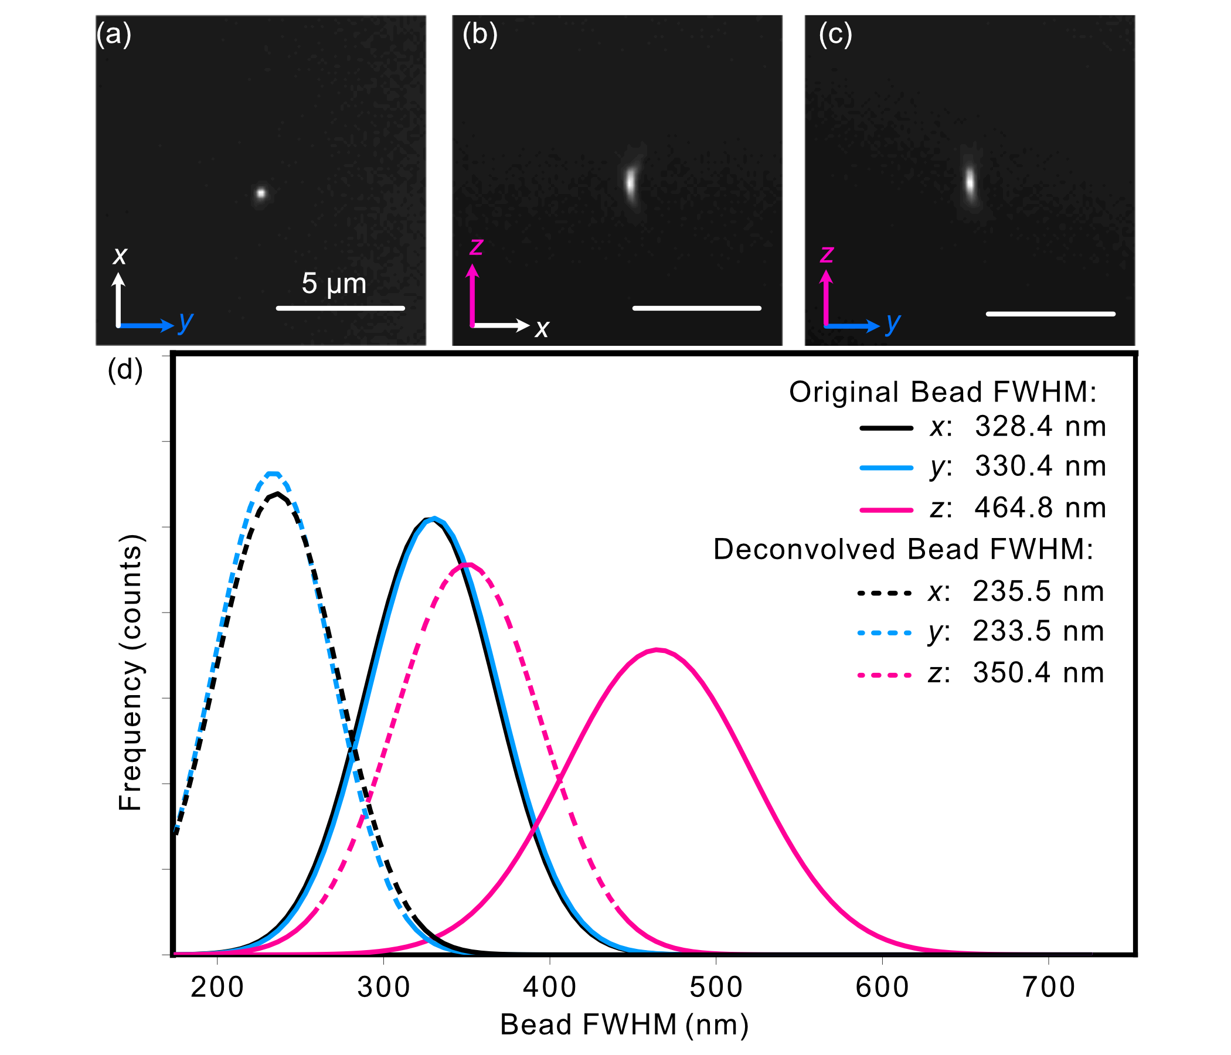
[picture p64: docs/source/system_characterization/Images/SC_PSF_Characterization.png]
Analysis of the experimental PSF characteristics


    **Figure 2:** Analysis of the experimental PSF characteristics

---------------

Sample Biological Images
______________________________

As a demonstration of Altair's biological imaging capabilities, we prepared and imaged mouse embryonic fibroblast
(MEF) cells, where multiple subcellular structures were stained for 4 different channels corresponding to the
excitation wavelengths of our laser source (405 nm, 488 nm, 561 nm, 638 nm). The staining protocol described in our
`initial Altair-LSFM paper <https://www.biorxiv.org/content/10.1101/2025.04.08.647739v1>`_ was
optimized for visualization of the nucleus (DAPI, 405 nm, cyan channel), microtubules (488 nm,
gray channel), actin filaments (561 nm, gold channel), and the Golgi apparatus of the MEF cells (638 nm, magenta
channel).

A deconvolved maximum intensity projection of a distribution of MEF cells is shown below in (a) and (f), with each
individual channel displayed in (b-e) and (g-j). These results display fine nucleolar features within the
nucleus, well-defined perinuclear Golgi structures, well-resolved stress fibers in the actin channel, and individually distinct microtubules, demonstrating Altair's ability to capture high-resolution images of cytoskeletal structures.

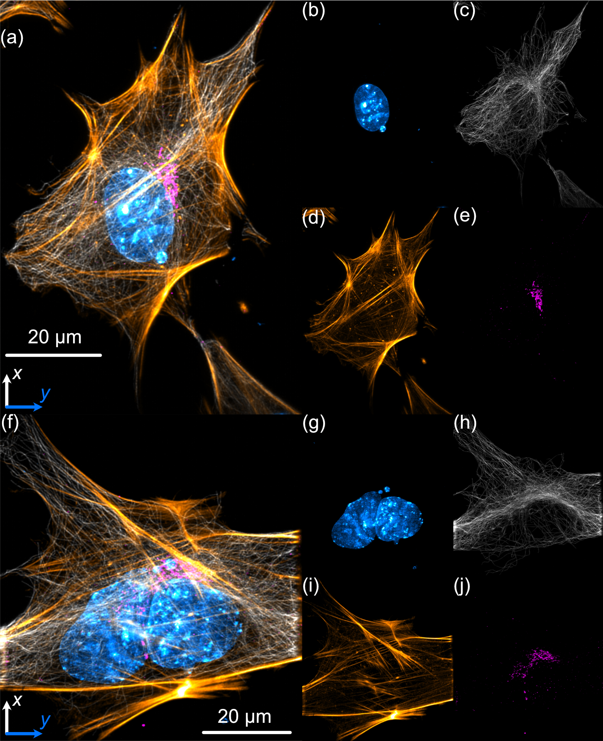
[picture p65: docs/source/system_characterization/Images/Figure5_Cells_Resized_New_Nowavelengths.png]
Analysis of MEF Cells


    **Figure 3:** Analysis of MEF Cells

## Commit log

2024-08-16 angle mount updates
2025-03-11 Organizing downloads
    [AngleMount.ipt, AngleMount.stl, AngleMount.stp, COMPASS_Baseplate_base.ipt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]
2025-03-11 link adjustments
    [OptimizedDesign_Baseplate.ipt, OptimizedDesign_Baseplate.stl]
2025-03-12 Adding in detection path assembly
